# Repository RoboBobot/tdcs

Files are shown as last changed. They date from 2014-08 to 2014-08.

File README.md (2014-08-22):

# An LT3092 based tDCS driver

# WARNING: Currently un-tested.

## Main Features

* Adjustable current from 0.7mA to 2.1mA. 
* Adjustable voltage from 9V to 18V. Also banana jacks to accept other voltages.
* Clearly labeled Anode and Cathode banana jacks.
* Mostly through-hole parts, for easier assembly

## Tasteful PCB Artwork

Top!

Bottom!

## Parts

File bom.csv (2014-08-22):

Digi-Key Part Number | Manufacturer | Manufacturer Part Number | Customer Reference | Quantity 1 | Quantity 2 | Quantity 3 | Mfg Std Lead Time | Description | Comments | RoHS Status | Lead Free Status | REACH Status
CF14JT100KCT-ND | STACKPOLE ELECTRONICS INC (VA) | CF14JT100K | R1 | 1 | 0 | 0 | 12 Weeks | RES 100K OHM 1/4W 5% CARBON FILM | Alternate Packaging Exists | RoHS Compliant | Lead free | Unaffected Aug-2011
J110-ND | EMERSON NETWORK POWER CONNECTIVITY JOHNSON | 105-0753-001 |  | 2 | 0 | 0 | 6 Weeks | CONN JACK STD INSUL HORIZ BLACK |  | RoHS Compliant | Lead free | N/A
J109-ND | EMERSON NETWORK POWER CONNECTIVITY JOHNSON | 105-0752-001 |  | 2 | 0 | 0 | 6 Weeks | CONN JACK STD INSUL HORIZ RED |  | RoHS Compliant | Lead free | N/A
TL-5A-ND | B&K PRECISION | TL 5A |  | 1 | 0 | 0 | 8 Weeks | TEST LEADS 5A |  | Not applicable | Not applicable | Unaffected Jun-2011
PTE60-151B-102B2-ND | BOURNS INC | PTE60-151B-102B2 |  | 1 | 0 | 0 | 13 Weeks | POT SLIDE 1K OHM .2W 60MM |  | RoHS Compliant | Lead free | Unaffected Dec-2013
CF14JT470RCT-ND | STACKPOLE ELECTRONICS INC (VA) | CF14JT470R | R2 | 1 | 0 | 0 | 12 Weeks | RES 470 OHM 1/4W 5% CARBON FILM | Alternate Packaging Exists | RoHS Compliant | Lead free | Unaffected Aug-2011
360-2133-ND | NKK SWITCHES | SS12SDP2 |  | 2 | 0 | 0 | 5 Weeks | SW SLIDE MINI SPDT TOP ACT 30V |  | RoHS Compliant | Lead free | Unaffected Jun-2012
LT3092EST#PBF-ND | LINEAR TECHNOLOGY | LT3092EST#PBF |  | 1 | 0 | 0 | 4 Weeks | IC CURRENT SOURCE 1% SOT223-3 | Alternate Packaging Exists | RoHS Compliant | Lead free | Unaffected Dec-2013
BH9V-PC-ND | MEMORY PROTECTION DEVICES | BH9VPC | 9V HOLDER | 2 | 0 | 0 | 12 Weeks | HOLDER BATTERY 9V PC MOUNT |  | RoHS Compliant | Lead free | Unaffected Oct-2011

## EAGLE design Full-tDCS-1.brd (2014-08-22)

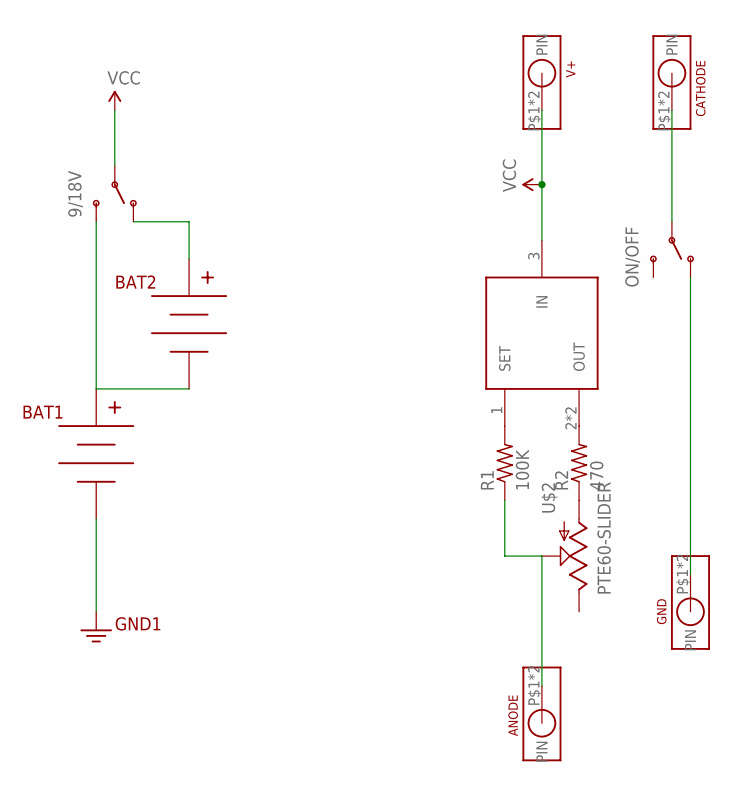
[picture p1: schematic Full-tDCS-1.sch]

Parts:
9/18V: SWITCH-SPDTPTH; SWITCH-SPDT
ANODE: BANANA-JACK; 105-0753-001-BANANA-JACK
BAT1, BAT2: BC9VPC
CATHODE: BANANA-JACK; 105-0753-001-BANANA-JACK
GND: BANANA-JACK; 105-0753-001-BANANA-JACK
ON/OFF: SWITCH-SPDTPTH; SWITCH-SPDT
R1: 100K; 0204/7
R2: 470; 0204/7
U$1: LT3092; SOT223
U$2: PTE60-SLIDER; SLIDER
V+: BANANA-JACK; 105-0753-001-BANANA-JACK

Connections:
GND: BAT1.V-, GND.P$1, GND.P$2, ON/OFF.1 (O)
unnamed: R1.2, U$1.1 (SET)
unnamed: R2.2, U$1.2 (OUT), U$1.4 (OUT)
unnamed: R2.1, U$2.1 (A)
unnamed: 9/18V.3 (S), BAT1.V+, BAT2.V-
unnamed: 9/18V.1 (O), BAT2.V+
unnamed: CATHODE.P$1, CATHODE.P$2, ON/OFF.2
unnamed: ANODE.P$1, ANODE.P$2, R1.1, U$2.2 (S)
VCC: 9/18V.2, U$1.3 (IN), V+.P$1, V+.P$2

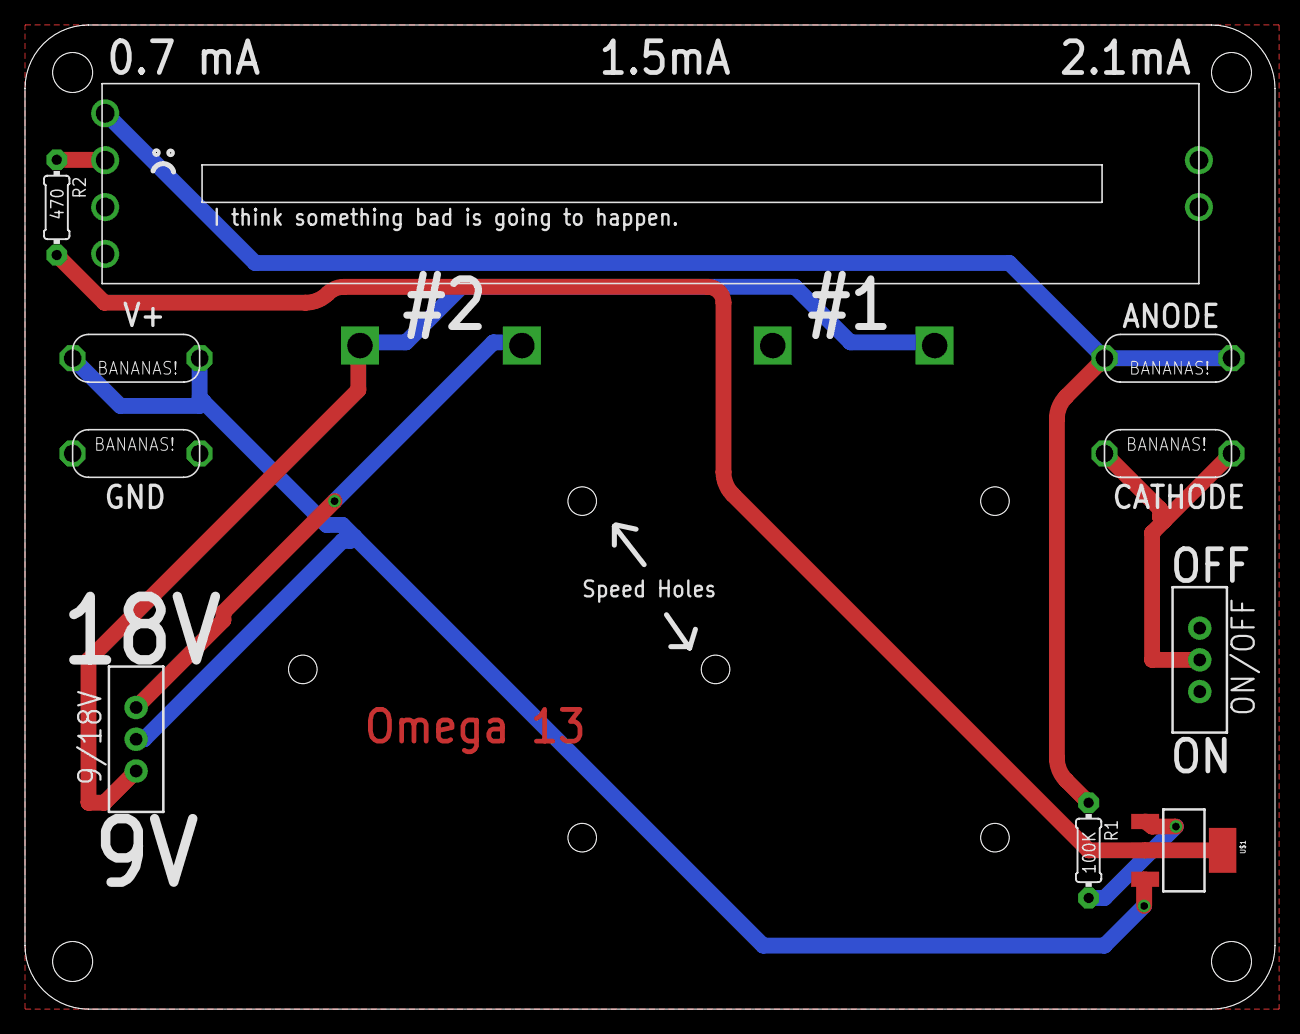
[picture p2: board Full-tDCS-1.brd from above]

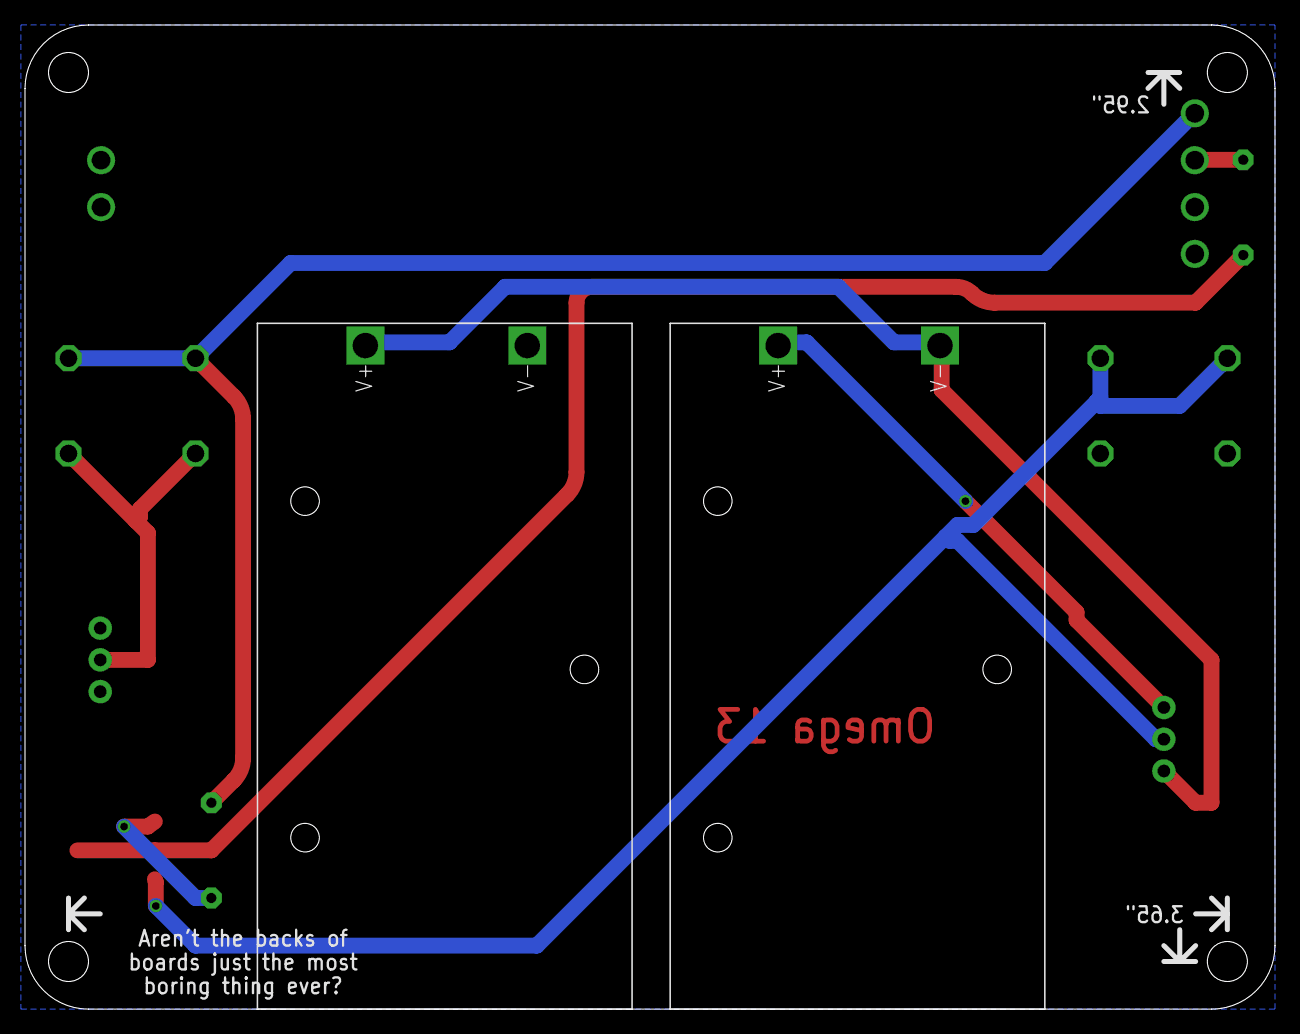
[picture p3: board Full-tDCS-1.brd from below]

Board: 2 copper layers, 100.0 x 78.7 mm, 12 parts (2 on the bottom side), 9 nets.

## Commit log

2014-08-22 BRD and SCH
    [Full-tDCS-1.brd, Full-tDCS-1.sch]
2014-08-22 Digikey BOM.
    [bom.csv]
2014-08-22 PCB artwork.

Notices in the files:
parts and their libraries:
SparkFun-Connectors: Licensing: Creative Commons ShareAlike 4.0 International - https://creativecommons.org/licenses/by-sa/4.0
